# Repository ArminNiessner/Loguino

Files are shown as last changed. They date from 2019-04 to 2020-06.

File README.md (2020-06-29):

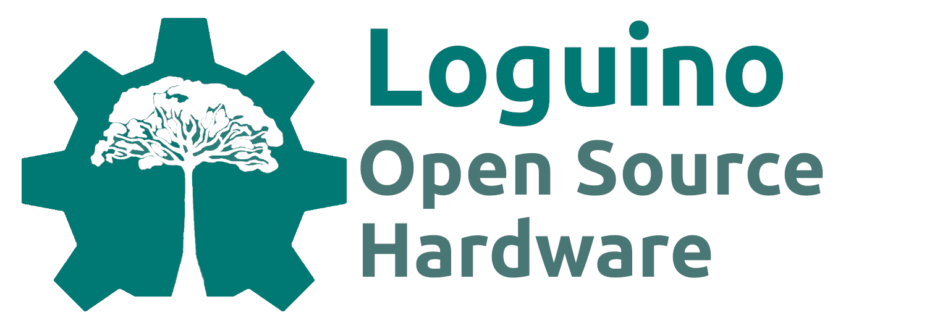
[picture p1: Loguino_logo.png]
Loguino Loguino Open Source Hardware


# Loguino



The Loguino is a low budget and open-source data acquisition device based on an Arduino Pro Mini and designed for monitoring e.g. tree growth dynamics, climate or other environmental parameters at remote locations. It is capable of reading analog inputs as voltage signals at a resolution of 18-bit and almost any kind of digital sensors can be connected using standard protocols (e.g. I²C, SPI, 1-Wire or SDI-12). Logging interval can be set from some seconds to hours and data are stored as comma seperated .csv file to a 4GB (or 8GB) micro sd-card. Therefore, no special software or hardware is needed to readout the Loguino. While the Loguino is in a low power sleep mode in between logs, consuming only about 100µA, a Real-Time-Clock Module (RTC DS3231) keeps track of time and wakens the Loguino for the next log event. Interrupts can independently be counted without interrupting main routines, in order to monitor rainfall or windspeed. The Loguino board togheter with a standard Lithium-Ion 18650 battery (keeps the Loguino running for about a year) is mounted within a rugged enclosure (IP65) that can be attached to a tree or pole, for instance.

The eagle files for the PCB are available in this repository and all parts are easily available on the internet, however, ready-to-use (assembled, programmed and tested) Loguinos are for sale by sending a request to armin.niessner@taysira.org. All Arduino libraries and sketches needed for operation of the Loguino are available in this repository or at other git repositories (listed below). The Arduino software needed to program the Loguino is available at [Arduino](https://www.arduino.cc/).

# Parts

* Arduino Pro Mini 3.3V, 8MHz, ATmega328 (e.g. [Amazon](https://www.amazon.de/gp/product/B078H9RMZY/ref=ppx_yo_dt_b_asin_title_o07_s01?ie=UTF8&psc=1))

* FTDI Adapter FT232RL USB to TTL Serial (3.3V, 5V) (e.g. [Amazon](https://www.amazon.de/AZDelivery-Adapter-FT232RL-Serial-gratis/dp/B01N9RZK6I/ref=sr_1_3?__mk_de_DE=%C3%85M%C3%85%C5%BD%C3%95%C3%91&keywords=FTDI&qid=1555957551&s=computers&sr=1-3))

* SPI micro sd-card shield (e.g. [Amazon](https://www.amazon.de/gp/product/B077MB17JB/ref=ppx_yo_dt_b_asin_title_o07_s00?ie=UTF8&psc=1))

* Real-Time-Clock RTC DS3231 (e.g. [Amazon](https://www.amazon.de/gp/product/B076GP5B94/ref=ppx_yo_dt_b_asin_title_o07_s02?ie=UTF8&psc=1))

* ADC MCP3424 (SOIC 14) 

* Screw terminals (5 x 5.08 mm 2pins, 4 x 2.54 mm 4 pins, 1 x 2.54 mm 3 pins, 1 x 2.54 mm 2 pins)

* Socket strip (6 pins, to connect the FTDI adapter)

* Pin strip (51 pins in total to place the Arduino Pro Mini onto the PCB and for placing the jumpers)

* Jumper (maximum 5)

* Resistors (2 x 10 KOhm, 3 x 4.7 KOhm, 4 x 2.2 KOhm)

* Ceramic capacitors (1 x 100 nF, 4 x 3.3 nF)

* Electrolytic capacitor (1 x 10µF)

* Micro sd-card (4 GB or 8 GB, quality may differ significantly between different manufacturer and even production lines, leading to a higher power consumption during sleep mode. I use and recommend Transcend TS4GUSDC4 Micro SDHC 4GB Class 4)

* Li-ion 18650 battery

* Li-ion 18650 battery tray

* Enclosure (Bopla ET 215 120 x 80 x 57)

* Cable glands (1-x, depending on number of cables to enter the enclosure)

* PCB (eagle files available in this repository or contact armin.niessner@taysira.org)

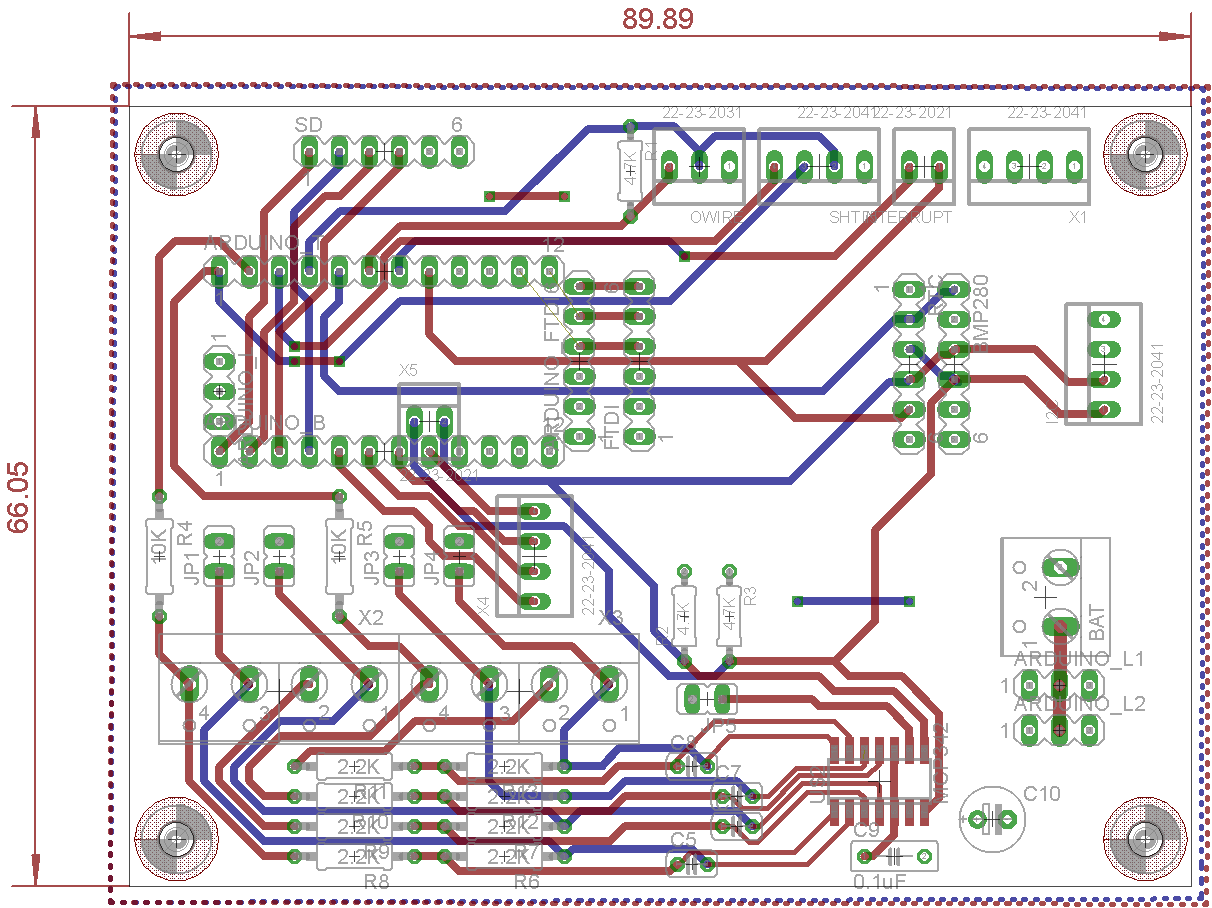
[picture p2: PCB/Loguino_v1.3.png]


# Assembly

1. Solder the Arduino Mini Pro Board on to the PCB using pins.

1. Remove the power LED and voltage regulator on the Arduino Pro Mini.

1. Solder the socket strip next to the Arduino Pro Mini for connection to the FTDI. Test the Arduino by uploading the first test sketch ("test_1_arduino.ino") and check the serial monitor for the output.

1. Prepare soldering areas for the ADC on the PCB with soldering fluid and solder the ADC MCP3424 onto the PCB.

1. Solder the two 4.7K Resistors, the 0.1µF ceramic capacitor, the 10µF ELKO and two pins next to the ADC. Place a bridge on the two pins.

1. Upload test script "test_2_adc.ino" and open serial monitor. The serial monitor should show random numbers for all four channels.

1. Solder all screw terminals, resistors, capacitors and pins onto PCB.

1. Repeat ADC test.

1. Remove voltage regulator from the SD-card-module, connect lower two pins with a piece of wire and remove the overlapping part of the SD-module-PCB under the pins using a "Dremel".

1. Solder the SD-module to the PCB and test it by uploading the test script "test_3_sd.ino". Check the serial monitor for error messages.

1. Remove the LED and upper resistor-IC from the RTC-module and solder the RTC-module to the PCB. Test it by uploading the script "test_4_rtc.ino" and check the serial monitor.

# Sensors



### Dendrometer (linear displacement potentiometer, MMR10_11 R5K, Megatron Elektronik AG & Co, Munich, Germany):

* Green = `ADC0 +` (left)

* Yellow = `ADC0 -` (middle)

* Red = `ADC1 +` (right)

* Connect `ADC0 -` and `ADC1 -` to GND (place jumper as shown in the picture above) 

Example sketch: [Loguino_dd_dd](https://github.com/ArminNiessner/Loguino/tree/master/sketches/Examples/Loguino_dd_dd/Loguino_dd_dd.ino)

### Thermocouple (Granier-sap-flow sensor):

* Connect one end to e.g. `ADC0 +` and the other end to `ADC0 -`

* leave the jumper at `ADC0 -` open

Example sketch: [Loguino_4xyl](https://github.com/ArminNiessner/Loguino/tree/master/sketches/Examples/Loguino_4xyl/Loguino_4xyl.ino)

### DS18S20 temperature:

* GND = `-` (right)

* VCC = `+` (middle)

* DATA = `D` (left)

Example sketch: [Loguino_dd_xyl_t](https://github.com/ArminNiessner/Loguino/tree/master/sketches/Examples/Loguino_dd_xyl_t/Loguino_dd_xyl_t.ino)

### DHT22 T/RH sensor:

* GND = `-` (right)
* VCC = `+` (second from right)
* Data = `D` (second from left)

Example sketch: [Loguino_DHT](https://github.com/ArminNiessner/Loguino/tree/master/sketches/Examples/Loguino_DHT/Loguino_DHT.ino)

### SHT7x Sensirion T/RH sensor:

* SCK = `C` (left, to Pin 7

* DATA = `D` (second from left)

* VCC = `+` (second from right)

* GND = `-` (right)

Example sketch: [Loguino_SHT](https://github.com/ArminNiessner/Loguino/tree/master/sketches/Examples/Loguino_SHT/Loguino_SHT.ino)

### BME280 T/RH/Pressure sensor:

* VCC = `+` (top)
* GND = `-` (second from top)
* SCL = `SCL` (third from top)
* SDA = `SDA` (third from bottom)

Example sketch: [Loguino_BME](https://github.com/ArminNiessner/Loguino/tree/master/sketches/Examples/Loguino_BME/Loguino_BME.ino)

# Software set up and programming the Loguino

1. Download and install the latest version of the [Arduino software](https://www.arduino.cc/en/Main/Software)
1. Download this repository (click on the green "clone"-button at the top of this web page) and copy all the folders in "libraries" from this repository to the "libraries"-folder in your Arduino installation folder.
1. Get the libraries [AVRUtils](https://github.com/SConaway/AVRUtils), [LowPower](https://github.com/rocketscream/Low-Power) and [SdFat](https://github.com/greiman/SdFat)
and copy them to the "libraries"-folder. If you want to use a DS18S20 temperature sensor or other digital sensors you have to get the corresponding library, listed below in the Libraries section.
1. Open one of the example scripts in the folder "sketches" from the Logiuno repository using the Arduino software. Go to "Tools" and 
set "Board" to "Arduino Pro or Pro Mini". Go again to "Tools" and set "Processor" to "ATmega 328P (3.3V, 8MHz)".
1. Connect the FTDI Adapter to the Loguino board, upper side facing the Arduino Pro Mini. Make sure
that the jumper on the FTDI Adapter is set to 3.3V and the battery is not connected to the Loguino. Connect the usb to a usb port and go to "Tools"
and set "Port" to the appropiate port (e.g. COM3). If you are using windows, you probably first need to download and install a driver for the FTDI Adapter
(e.g. [here](https://www.campbellsci.com/downloads/usb-to-serial-driver-ftdi-chip-set)).
1. "Upload" the sketch (right arrow button) and wait until the sketch is compiled and uploaded.
Open the "Serial Monitor" (button at the upper right corner) and check the output.

## Setting the time
1. Use the [test_4_rtc.ino](https://github.com/ArminNiessner/Loguino/tree/master/sketches/Tests/test_4_rtc/test_4_rtc.ino)
to set the RTC to your system time.
2. Upload the sketch, comment `RTC.adjust(DateTime(__DATE__, __TIME__));` and upload the sketch again. The second 
upload with `//RTC.adjust(DateTime(__DATE__, __TIME__));` should be right after the first upload was finished, in order
to have only a short delay between RTC time and system time (usually less than 10 seconds).

## Final setup
Choose an appropiate example sketch from this repository and adjust it to your sensor setup:

* `uint8_t Log_Interval_Minutes = 1;` set to the desired logging intervall in minutes
* `String file_ini = "Lg0001";` set to the appropiate Logger ID
* If you want that logging starts at the next full minute, next full 10 minute (:00, :10, :20, ..),
next full half hour (:00, :30) or the next full hour, you can uncomment the appropiate block of coder
under `void setup() {....}` and uncomment the other blocks. 

Upload the sketch and your Loguino is ready to go.

## Libraries

* AVRUtils ([Git](https://github.com/SConaway/AVRUtils)) - measure supply voltage

* SPI ([Arduino](https://www.arduino.cc/en/reference/SPI)) - communication with SD-card module

* SdFat ([Git](https://github.com/greiman/SdFat)) - read and write to SD-card

* Wire ([Arduino](https://www.arduino.cc/en/reference/wire)) - communication with I²C devices e.g. the MCP3424

* LowPower ([Git](https://github.com/rocketscream/Low-Power)) - low power library to set Loguino to sleep

* ANiess (available in this repository) - main library for Loguino

* AN_RTClib (available in this repository) - library to interact with RTC

* MCP342x (available in this repository) - library to interact with the ADC

* DallasTemperature ([Git](https://github.com/milesburton/Arduino-Temperature-Control-Library))- library to interact with the DS18S20 temperature sensor

* Sensirion ([Git](https://github.com/spease/Sensirion)) - library to interact with the SHT75 T/RH sensor

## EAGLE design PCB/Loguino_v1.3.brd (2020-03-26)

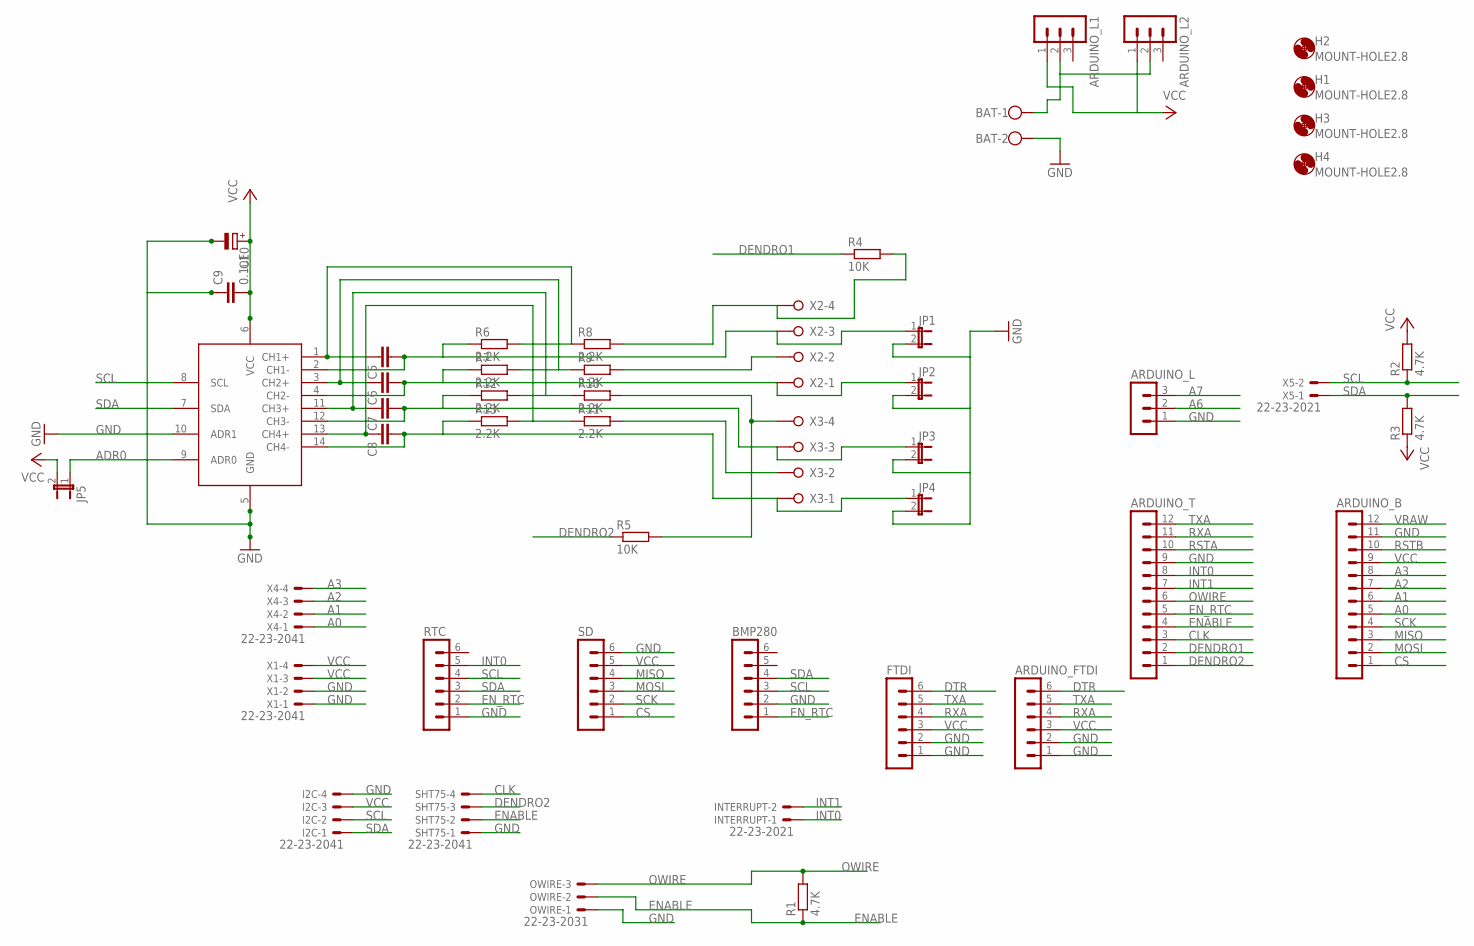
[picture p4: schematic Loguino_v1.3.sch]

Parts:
ARDUINO_B: MA12-1
ARDUINO_FTDI: MA06-1
ARDUINO_L, ARDUINO_L1, ARDUINO_L2: MA03-1
ARDUINO_T: MA12-1
BAT: W237-102
BMP280: MA06-1
C5, C6, C7, C8: C-EU025-024X044; C025-024X044
C9: 0.1uF; C050-025X075
C10: CPOL-EUE2,5-6E; E2,5-6E
FTDI: MA06-1
H1, H2, H3, H4: MOUNT-HOLE2.8; 2,8
I2C: 22-23-2041
INTERRUPT: 22-23-2021
JP1, JP2, JP3, JP4, JP5: JP1E; JP1
OWIRE: 22-23-2031
R1, R2, R3: 4.7K; 0204/7
R4, R5: 10K; 0207/10
R6, R7, R8, R9, R10, R11, R12, R13: 2.2K; 0207/10
RTC: MA06-1
SD: MA06-1
SHT75: 22-23-2041
U$2: MCP342; SO14
X1, X4: 22-23-2041
X2, X3: W237-04P; W237-4P
X5: 22-23-2021

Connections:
A0: ARDUINO_B.5, X4.1
A1: ARDUINO_B.6, X4.2
A2: ARDUINO_B.7, X4.3
A3: ARDUINO_B.8, X4.4
A6: ARDUINO_L.2
A7: ARDUINO_L.3
ADR0: JP5.1, U$2.9 (ADR0)
CLK: ARDUINO_T.3, SHT75.4
CS: ARDUINO_B.1, SD.1
DENDRO1: ARDUINO_T.2, R4.1
DENDRO2: ARDUINO_T.1, R5.1, SHT75.3
DTR: ARDUINO_FTDI.6, FTDI.6
ENABLE: ARDUINO_T.4, OWIRE.2, R1.1, SHT75.2
EN_RTC: ARDUINO_T.5, BMP280.1, RTC.2
GND: ARDUINO_B.11, ARDUINO_FTDI.1, ARDUINO_FTDI.2, ARDUINO_L.1, ARDUINO_T.9, BAT.2, BMP280.2, C9.1, C10.-, FTDI.1, FTDI.2, I2C.4, JP1.2, JP2.2, JP3.2, JP4.2, OWIRE.1, RTC.1, SD.6, SHT75.1, U$2.5 (GND), U$2.10 (ADR1), X1.1, X1.2
INT0: ARDUINO_T.8, INTERRUPT.1, RTC.5
INT1: ARDUINO_T.7, INTERRUPT.2
MISO: ARDUINO_B.3, SD.4
MOSI: ARDUINO_B.2, SD.3
unnamed: ARDUINO_L1.2, ARDUINO_L2.2, BAT.1
unnamed: C5.2, JP1.1, R6.1, U$2.2 (CH1-), X2.3
unnamed: R4.2, R8.2, X2.4
unnamed: R9.2, X2.2
unnamed: R5.2, R10.2, X3.4
unnamed: R11.2, X3.2
unnamed: C5.1, R6.2, R8.1, U$2.1 (CH1+)
unnamed: C6.1, R7.2, R9.1, U$2.3 (CH2+)
unnamed: C7.1, R10.1, R12.2, U$2.11 (CH3+)
unnamed: C8.1, R11.1, R13.2, U$2.13 (CH4+)
unnamed: C6.2, JP2.1, R7.1, U$2.4 (CH2-), X2.1
unnamed: C7.2, JP3.1, R12.1, U$2.12 (CH3-), X3.3
unnamed: C8.2, JP4.1, R13.1, U$2.14 (CH4-), X3.1
OWIRE: ARDUINO_T.6, OWIRE.3, R1.2
RSTA: ARDUINO_T.10
RSTB: ARDUINO_B.10
RXA: ARDUINO_FTDI.4, ARDUINO_T.11, FTDI.4
SCK: ARDUINO_B.4, SD.2
SCL: BMP280.3, I2C.2, R2.1, RTC.4, U$2.8 (SCL), X5.2
SDA: BMP280.4, I2C.1, R3.2, RTC.3, U$2.7 (SDA), X5.1
TXA: ARDUINO_FTDI.5, ARDUINO_T.12, FTDI.5
VCC: ARDUINO_B.9, ARDUINO_FTDI.3, ARDUINO_L1.1, ARDUINO_L2.1, C9.2, C10.+, FTDI.3, I2C.3, JP5.2, R2.2, R3.1, SD.5, U$2.6 (VCC), X1.3, X1.4
VRAW: ARDUINO_B.12

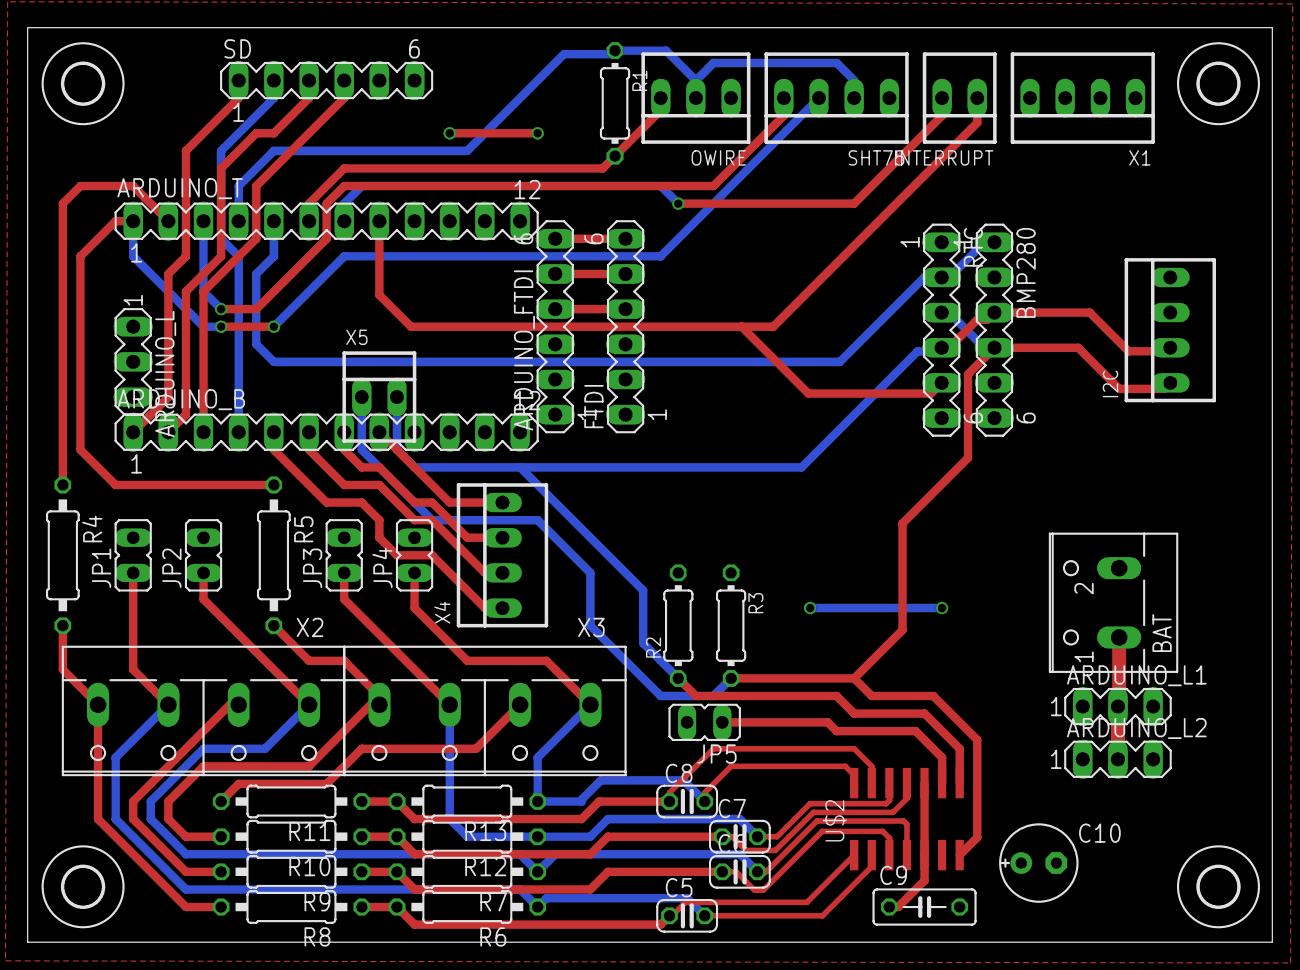
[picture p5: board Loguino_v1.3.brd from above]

Board: 2 copper layers, 89.9 x 66.0 mm, 49 parts (0 on the bottom side), 37 nets.

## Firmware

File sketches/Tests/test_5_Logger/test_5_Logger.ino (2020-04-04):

/*
 * Example sketch to test if logging routine is working
 * 
 * Copyright (C) 2019  Armin Niessner
 *
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
 *  You should have received a copy of the GNU General Public License
 *  along with this program. If not, see <https://www.gnu.org/licenses/>.
 */

#include <Wire.h>                       // lib for I2C (needed for ADC)
#include <SPI.h>                        // lib for SPI (needed for SD-Card module
#include "SdFat.h"                      // lib for SD-Card
#include <ANiess.h>               // needed for RTC
#include <AN_RTClib.h>                     // lib for Real-Time-Clock
#include <LowPower.h>                   // lib for sleep mode/low power mode
#include <AVRUtils.h>                   // needed to messure supply voltage
#include <DallasTemperature.h>          // lib for DS18S20 Temperature sensor
#include <MCP342x.h>                    // lib for ADC

#define ONE_WIRE_BUS 4                  // data pin for DS18S20
OneWire oneWire(ONE_WIRE_BUS);          
DallasTemperature sensors(&oneWire);   

AVRUtils avr;
DS3231 RTC;

SdFat SD;

#define SD_CS_PIN SS

File dataFile;
unsigned long Filesize;

//const int chipSelect = 10;              // pin chipselect for SD-Card
const int enable_rtc = 5;               // pin to enable power supply to RTC
const int enable_temp = 6;              // pin to enable power supply to DS18S20
const int enable_dd1 = 8;               // pin to enable power supply to Dendrometer #1
//const int enable_dd2 = 9;             // pin to enable power supply to Dendrometer #2

uint8_t Log_Hour;                       // variable for hour to log
uint8_t Log_Minute;                     // variable for minute to log
uint8_t st_Hour;                        // variable for hour at logger start
uint8_t st_Minute;                      // variable for minute at logger start
uint8_t Log_Interval_Minutes = 1;       // logging intervall in minutes

int wakePin = 2;                 // pin used for waking up

const byte addr = 4;                    // ADC: I2C address - 0:68, 1:69, 2:6A, 3:6B, 4:6C, 5:6D, 6:6E, 7:6F
const uint8_t gain = 0;                 // ADC: gain factor 0-3: x1, x2, x4, x8
const uint8_t rate = 3;                 // ADC: resolution 0-3: 12bit ... 18bit
const uint8_t mode = 0;                 // ADC: mode 0 == one-shot mode - 1 == continuos mode

MCP342x mcp342x = MCP342x();            //  create an objcet of the class MCP342x

int i_file = 0;                         // initial file appendix (a new file will be created for every 1MB file size)
String app;
String filename;   
String file_ini = "Lg0001";             // set to serial number of the Loguino    
float vdd1;                             // voltage dd1
float dd1;                              // cm dd1
char str_dd1[10] = "";
float batV;                             // Battery voltage, supply voltage
char str_batV[10] = "";
float xyl1;                             // xylem sensor #1
char str_xyl1[10] = "";

float temp;

void dateTime(uint16_t* date, uint16_t* time) {
  DateTime now = RTC.now();

  // return date using FAT_DATE macro to format fields
  *date = FAT_DATE(now.year(), now.month(), now.day());

  // return time using FAT_TIME macro to format fields
  *time = FAT_TIME(now.hour()-2, now.minute(), now.second());
}

void setup() {
  pinMode(enable_rtc, OUTPUT);          // enable RTC
  digitalWrite(enable_rtc, HIGH); 
  pinMode(enable_temp, OUTPUT); 
  pinMode(enable_dd1, OUTPUT); 
  pinMode(wakePin, INPUT_PULLUP);
  Serial.begin(9600);
  delay(1000); // let serial console settle
  Wire.begin();
  RTC.begin();
  avr.begin();
  
  DateTime now = RTC.now();
  st_Hour = now.hour();
  st_Minute = now.minute();

//  if (st_Minute > 30) {               // uncomment if log intervall is 30 min and logs should be at :00 and :30
//    Log_Hour = st_Hour +1;
//    Log_Minute = 0;
//  } else {
//    Log_Hour = st_Hour;
//    Log_Minute = 30;
//  }

//  Log_Minute = (st_Minute / 10 + 1) * 10; // uncomment if logging should start at next :00, :10, ;20, :30, :40, 50 minute
//  Log_Hour = st_Hour;
//  if (Log_Minute == 60) {
//    Log_Hour = st_Hour + 1;
//    Log_Minute = 0;
//  }

//  Log_Hour = st_Hour + 1;             // uncomment if logging should start at :00 (next full hour)
//  Log_Minute = 0;

  Log_Hour = st_Hour;                   // logging starts within a minute
  Log_Minute = st_Minute + 1;

  Serial.print("Current Time: ");
  Serial.print(st_Hour);                // just to check if RTC is set right
  Serial.print(":");
  Serial.println(st_Minute);
  Serial.print("Next scheduled log: ");
  Serial.print(Log_Hour);
  Serial.print(":");
  Serial.println(Log_Minute);

  Serial.print("Initializing SD card...");    // see if the card is present and can be initialized:
  if (!SD.begin(SD_CS_PIN)) {
    Serial.println("Card failed, or not present");
    // don't do anything more:
    return;
  }
  Serial.println("card initialized.");

  measure();                            // make a measurement at logger start outside logging routine
 
  delay(500);
  digitalWrite(enable_rtc, LOW);        // disable RTC voltage supply
}

void loop() {
  
  digitalWrite(enable_rtc, HIGH);       // enable RTC voltage supply
  DateTime now = RTC.now();
  if(Log_Hour == now.hour() && Log_Minute == now.minute()) {          // check if current time equals time to log
    measure();                          // execute logging routine
    
    Log_Minute += Log_Interval_Minutes;       // set next time to log
    if (Log_Minute >= 60) {                   // adjust minute count if reaches 60
      Log_Minute -= 60;
      Log_Hour += 1;
      
      if (Log_Hour == 24) {                   // adjust hour count if reaches 24
        Log_Hour = 0;               
      }
    }
  }

  RTC.disableInterrupts();                // clear RTC interrupts
  RTC.clearINTStatus(); 
  RTC.enableInterrupts(Log_Hour, Log_Minute,0);   // set RTC interrupt to next due time

  delay(500);                            
  digitalWrite(enable_rtc, LOW);          // disable RTC voltage supply
  sleepNow();                             // enter sleep mode (will be waked up from RTC at time to log)
}

void measure() {
  DateTime now = RTC.now();               
  delay(200);
  SD.begin(SD_CS_PIN);                   // initiate comunication to SD-Card
    
  delay(50);
  
  digitalWrite(enable_temp, HIGH);        // enable voltage supply to DS18S20
  digitalWrite(enable_dd1, HIGH);         // enable voltage supply to Dendrometer #1

  delay(50);

  // meassure Dendrometer #1
  mcp342x.setConf(addr, 1, 0, mode, rate, gain); //Measure total voltage (channel 0)
  delay(300);                                   // extend delay if conversion fails!!!!
  vdd1 = mcp342x.getData(addr);
  delay(50);

  mcp342x.setConf(addr, 1, 1, mode, rate, gain); //Measure partial voltage (channel 1)
  delay(300);
  dd1 = mcp342x.getData(addr) / vdd1;
  dtostrf(dd1, 5, 4, str_dd1);
  delay(50);
  
  batV = avr.getAVRVcc() / 1000;      // meassure battery/supply voltage in V
  dtostrf(batV, 4, 3, str_batV);

  sensors.requestTemperatures();      // meassure temperature
  delay(500);
  temp = sensors.getTempCByIndex(0);  // sensor at address 0

  mcp342x.setConf(addr, 1, 2, mode, rate, 3); //Measure voltage of channel 2 (e.g. for thermocouple)
  delay(300);
  xyl1 = mcp342x.getData(addr) * 1000000 / 40;    // convert µV in deltaT
  dtostrf(xyl1, 5, 4, str_xyl1);
  delay(50);
  
  digitalWrite(enable_temp,LOW);         
  digitalWrite(enable_dd1, LOW);    

  app = print2digitsstr(i_file);
  filename = String(file_ini + app + ".txt");

  SdFile::dateTimeCallback(dateTime);
  dataFile = SD.open(filename.c_str(), FILE_WRITE);             // open file in write mode
  Filesize = dataFile.size();             // get size of file
  
  if (Filesize > 1000000 && dataFile) {
    dataFile.close();
    i_file += 1;
    app = print2digitsstr(i_file);
    filename = String(file_ini + app + ".txt");
    SdFile::dateTimeCallback(dateTime);
    dataFile = SD.open(filename.c_str(), FILE_WRITE);
    Filesize = dataFile.size();
  }
    
  if (Filesize == 0 && dataFile) {
    dataFile.println("Date,dd1,xyl1,temp,battV");         // if File is empty (new), create header
  } else { 
  }
  if (dataFile) {
    
    print2digitsf(now.year());
    dataFile.print("-");
    print2digitsf(now.month());
    dataFile.print("-");
    print2digitsf(now.day());
    dataFile.print(" ");
    print2digitsf(now.hour());
    dataFile.print(":");
    print2digitsf(now.minute());
    dataFile.print(":");
    print2digitsf(now.second());
    dataFile.print(",");
    dataFile.print(str_dd1);
    dataFile.print(",");
    dataFile.print(str_xyl1);
    dataFile.print(",");
    dataFile.print(temp);
    dataFile.print(",");
    dataFile.println(str_batV);
    dataFile.close();
    
  } else {
    Serial.println("Error opening File"); 
  }

  print2digits(now.year());
  Serial.print("-");
  print2digits(now.month());
  Serial.print("-");
  print2digits(now.day());
  Serial.print(" ");
  print2digits(now.hour());
  Serial.print(":");
  print2digits(now.minute());
  Serial.print(":");
  print2digits(now.second());
  Serial.print(",");
  Serial.print(str_dd1);
  Serial.print(",");
  Serial.print(str_xyl1);
  Serial.print(",");
  Serial.print(temp);
  Serial.print(",");
  Serial.println(str_batV);
}

void sleepNow() {
    attachInterrupt(0, wakeup, LOW);
    delay(100);
    LowPower.powerDown(SLEEP_FOREVER, ADC_OFF, BOD_OFF); // deep sleep  
}

void wakeup(void) {
  detachInterrupt(0); // detach interrupt on wakeup 
  delay(100);
}

// functions to print numbers in date and time as two digits (e.g. 06 instead of 6)
void print2digitsf(int number) {
  if (number >= 0 && number < 10) {
    dataFile.write('0');
  }
  dataFile.print(number, DEC);
}

void print2digits(int number) {
  if (number >= 0 && number < 10) {
    Serial.write('0');
  }
  Serial.print(number, DEC);
}

String print2digitsstr(int number) {
  String result;
  if (number >= 0 && number < 10) {
    result = "0" + String(number);
  } else {
    result = String(number);
  }
  return result;
}

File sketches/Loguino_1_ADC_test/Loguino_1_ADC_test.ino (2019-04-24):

/*
 * Reads the value from an AD converter MCP342x and displays it in the serial monitor
 * 
 * Copyright (C) 2019  Armin Niessner
 *
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
 *  You should have received a copy of the GNU General Public License
 *  along with this program. If not, see <https://www.gnu.org/licenses/>.
 */
 
#include <Wire.h>
#include <MCP342x.h>

const byte addr = 4;      // ADC: I2C address - 0:68, 1:69, 2:6A, 3:6B, 4:6C, 5:6D, 6:6E, 7:6F
const uint8_t gain = 0;   // ADC: gain factor 0-3: x1, x2, x4, x8
const uint8_t rate = 3;   // ADC: resolution 0-3: 12bit ... 18bit
const uint8_t mode = 0;   // ADC: mode 0 == one-shot mode - 1 == continuos mode
//  create an objcet of the class MCP342x
MCP342x mcp342x = MCP342x();

const uint8_t enable = 8;   // connected to ch0+ via a 10K resistor

float span = 0.0;
char str_buf[50] = "                            ";

void setup()
{
  Serial.begin(9600);
  pinMode(enable, OUTPUT);
  Serial.print("General Call Reset... ");
  Wire.beginTransmission(B00000000);
  Wire.write(B00000110);
  Wire.endTransmission();
  Serial.println("fertig");
  
}



void loop()
{
 
  digitalWrite(enable, HIGH);
  for(uint8_t ch=0; ch<4;ch++){
    if(ch)
      Serial.print("\t");
      Serial.print("C ");
      Serial.print(ch);
      mcp342x.setConf(addr, 1, ch, mode, rate, gain);
      delay(300);
      span = mcp342x.getData(addr);
  
      //  convert float to char[]
      dtostrf(span, 10, 6, str_buf);
  
      Serial.print(str_buf);
  }
  Serial.println();

  digitalWrite(enable, LOW); 

   
  //  do it every n milliseconds
  delay(2000);
}

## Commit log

2019-04-22 sketches for Arduino added
2019-04-22 eagle PCB files added
    [Loguino_mini.brd, Loguino_mini.sch, Loguino_mini_v1.2.brd, Loguino_mini_v1.2.sch]
2020-03-26 updated PCB and sketches to v1.3
    [Loguino_mini.brd, Loguino_mini_v1.2.sch, Loguino_v1.3.brd, Loguino_v1.3.sch]

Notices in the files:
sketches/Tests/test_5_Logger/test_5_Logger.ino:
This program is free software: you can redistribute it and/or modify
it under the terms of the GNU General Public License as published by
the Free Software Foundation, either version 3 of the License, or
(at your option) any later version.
